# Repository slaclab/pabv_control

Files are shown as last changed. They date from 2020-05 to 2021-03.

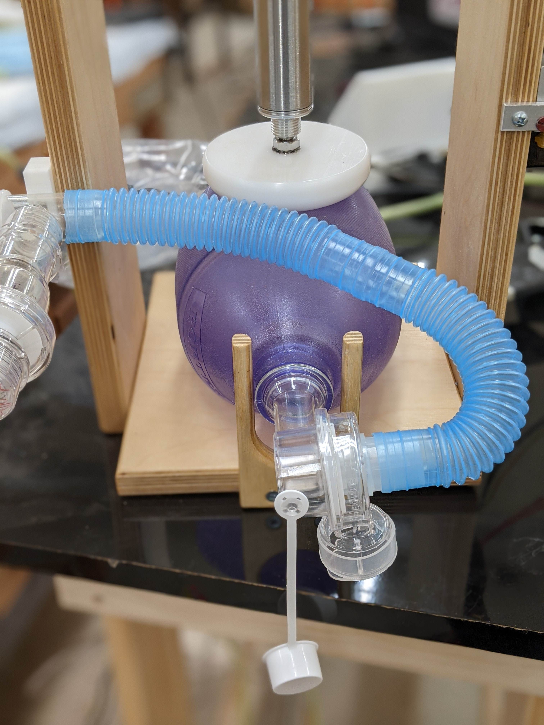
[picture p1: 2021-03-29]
ASV IP folder/Photos of assembled parts/PXL_20200915_001322814.PORTRAIT-01.COVER.jpg

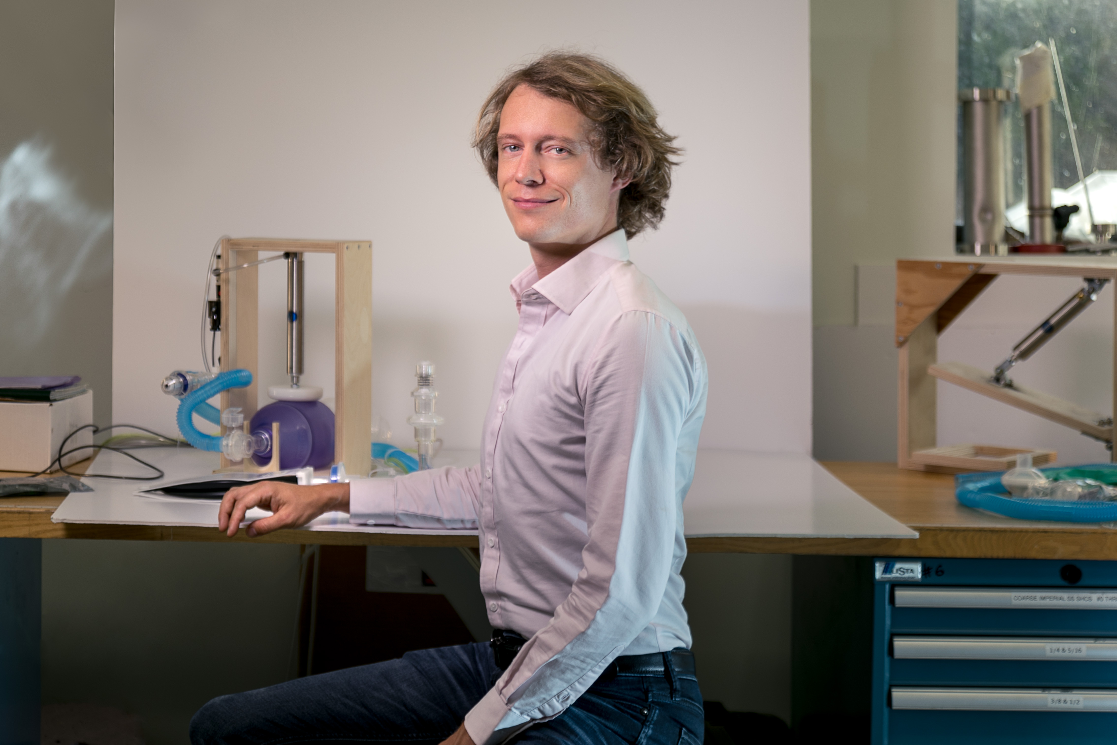
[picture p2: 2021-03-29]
ASV IP folder/Media materials/2020_0710_IR2_Ventilator_Gamazo_8752.jpg

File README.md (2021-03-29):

# Overview

This repository contains all hardware descriptions and software to build and control the SLAC
Acute Shortage Ventilator (ASV) developed to battle against the Covid crisis on a global scale.

All information on the project can be found at:

- [Media Announcement](https://www6.slac.stanford.edu/news/2020-08-13-slac-scientists-invent-low-cost-emergency-ventilator-and-share-design-free.aspx)
- [Official Paper](https://www.medrxiv.org/content/10.1101/2020.07.20.20158147v1)
- [Technology](http://techfinder.stanford.edu/technologies/S20-256_acute-shortage-ventilator)
- [DOECode](https://www.osti.gov/doecode/biblio/52411)
- [ASV Website](https://www.slac-asv.net/)

Documentation can also be found in the ASV IP folder directory of this repository

The content in this repository is licensed under a BSD 3-clause License. See LICENSE.txt for detail.

# Installation
### Getting the Code and dependencies
1. Install Anaconda3 (64-bit) for Windows 10 from here:
   https://www.anaconda.com/products/individual
and open a Anaconda Prompt
2. `conda install -y -c conda-forge git pyinstaller pyserial pyqt pyqtgraph`
3. `git clone https://github.com/slaclab/pabv_control`
4. `cd pabv_control`  
5. We now use submodules for various libraries, run this to pull them  
   `git submodule update --init --recursive`
##### Downloading arduin-cli
5. `bootstrap.py`
##### Compiling all sketches
6. `board_compile.py`

### Tested platforms
1.    Windows 10 64-bit
2.    Windows 10 32-bit
3.    Linux 64-bit
4.    MacOSX 64-bit

- Excutables built on Windows 10 32-bit may run on Windows 10 64-bit. Windows 7 or 8 support would require a native build.

### Packing the python client for distribution
- simply run the packaging scripts
- `pkg_gui.py`

### Wrapper scripts for arduino CLI

##### Show connected boards
- `board_list.py`
- this will create a standalone executable that can be copied to a USB stick

= example filename: `dist\client_py_Windows_64bit_v0.0.2-50-g3790d7b.exe`

Example output for an UNO

`Port Type              Board Name  FQBN            Core`

`COM3 Serial Port (USB) Arduino Uno arduino:avr:uno arduino:avr`

##### Upload compiled sketch
- `board_upload.py COM3 ambu_control_flow_cal`

Example output:

`Uploading sketch ambu_control_flow_cal to port COM3`

### Getting Running
- In Anaconda Prompt  
  - `cd pabv_control/python_client`  
  - `python client.py`

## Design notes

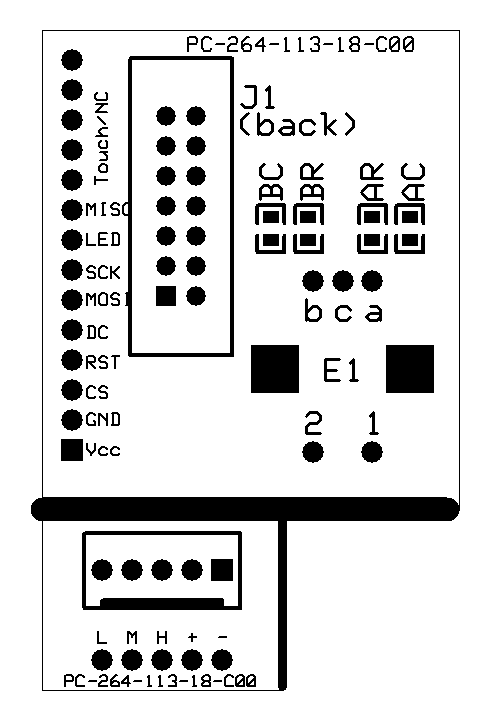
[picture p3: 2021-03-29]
ASV IP folder/Electronics/NanoShield_V03_breakouts.bmp

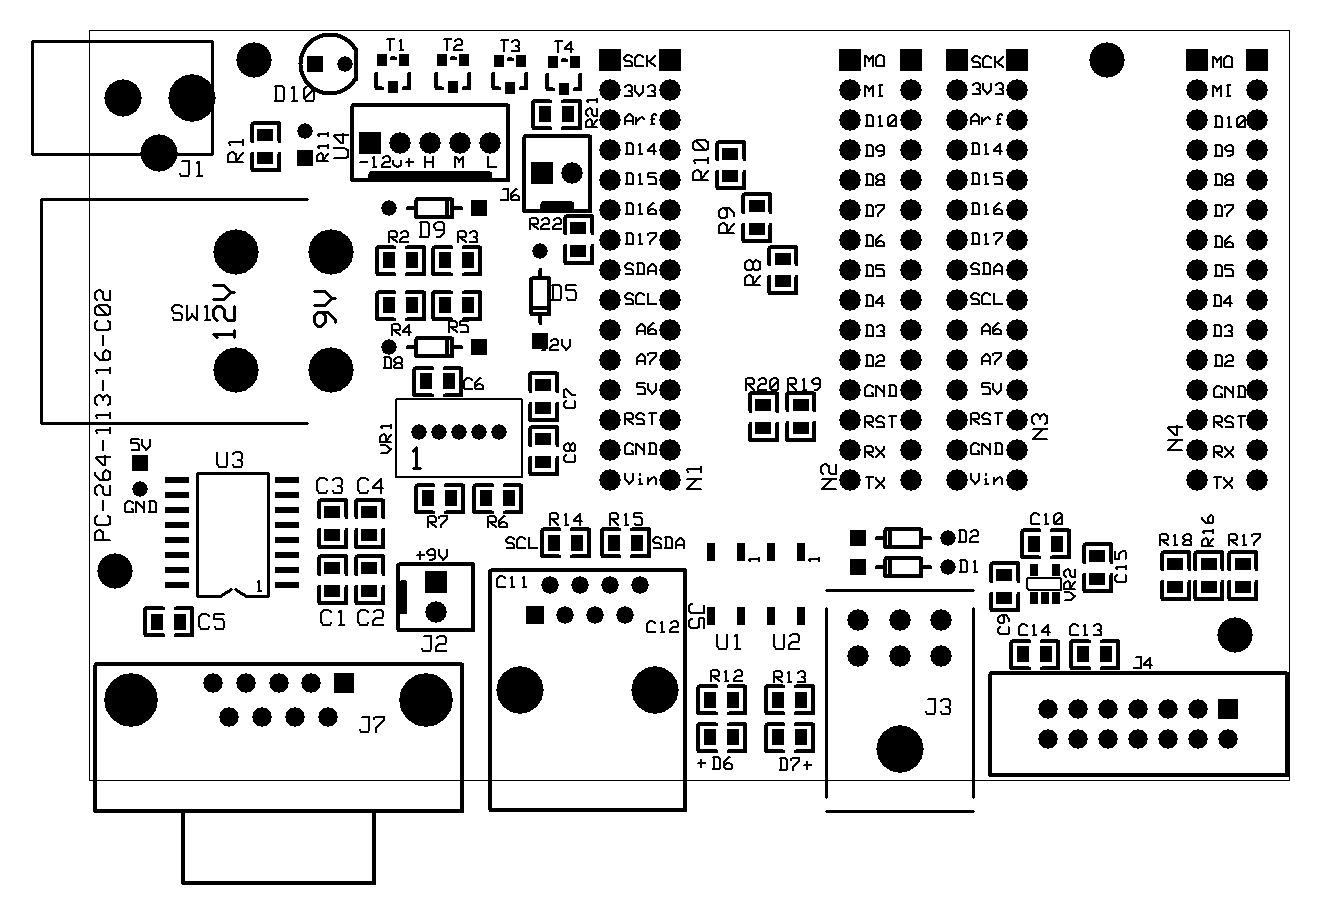
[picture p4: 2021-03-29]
ASV IP folder/Electronics/NanoShield_V03_pcb.bmp

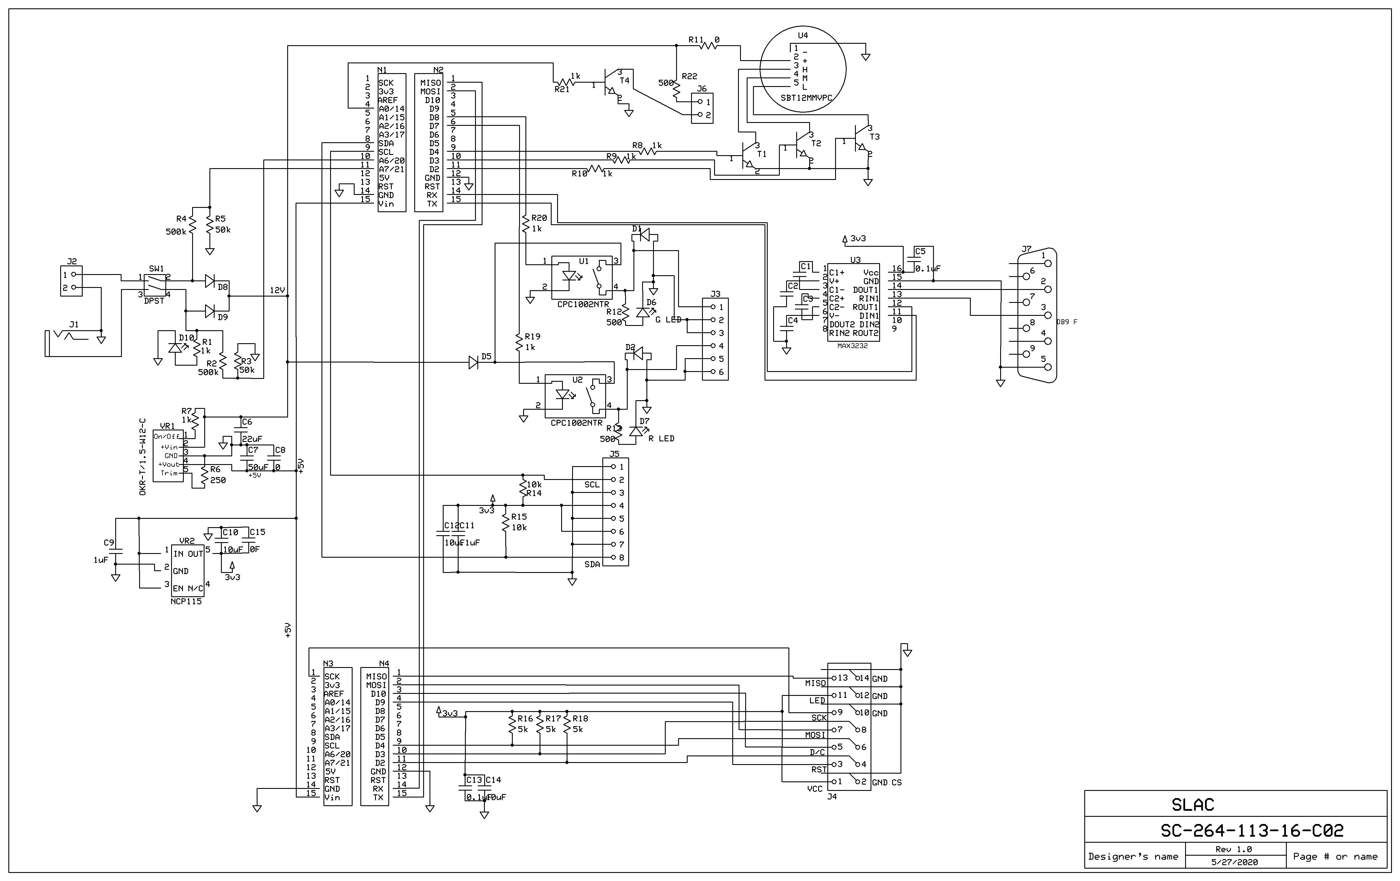
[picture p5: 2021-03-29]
ASV IP folder/Electronics/NanoShield_V03.bmp

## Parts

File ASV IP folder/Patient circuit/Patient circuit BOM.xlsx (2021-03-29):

Description | Link | Unit price | Qty | Total | Notes
PEEP valve | https://www.medline.com/sku/item/MDPPTX8501 | $22.26 | 2 | $44.53
HME filter | https://www.medline.com/sku/item/MDPDYNJAAHME1 | $2.12 | 1 | $2.12
MRI active patient circuit | https://www.medline.com/sku/item/MDPDYNJAA300NF | $23.64 | 1 | $23.64
Manual resuscitator w/ reservoir bag | https://www.medline.com/sku/item/MDPPTX8500P | $40.84 | 1 | $40.84
Straight connector with pressure port | https://www.medline.com/sku/item/MDPBXT004081 | $1.91 | 1 | $1.91
22-15-22 mm aerosol tee connector | https://www.medline.com/sku/item/MDPWST219 | $0.51 | 1 | $0.51
22mm cuff connector | https://www.medline.com/sku/item/MDPBXT001821 | $0.98 | 3 | $2.94
Exhalation filter | https://mms.mckesson.com/product/508994/Vyaire-Medical-303HEPA | $9.66 | 1 | $9.66
Spirometer | Alpha source inc p/n 8004382 (https://www.alphasource.com/) | $14.30 | 1 | $14.30
 |  |  | Total | $140.44

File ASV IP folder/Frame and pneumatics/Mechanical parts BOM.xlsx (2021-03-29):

Pneumatics | Seller | Part number | Cost
1/4" Polyflow Tube
3 way solenoid valve | Automation Direct | AVS-3312-24D | 35
Flow Control Valve OUT | Automation Direct | FVS14-18N | 6.5
Flow Control Valve IN | Automation Direct | FVR14-18N | 6.5
1/8in NPT Push2Connect | Automation Direct | MS14-18N
12V solenoid (to convert) | Automation Direct | AVC2-12D | 8.25
Binary Valve | Amazon | Beduan 2 Way Normally Closed DC 12V Electric Solenoid Air Valve 1/8" NPT | 11 | https://www.amazon.com/dp/B07N2DZ5FP/ref=pe_2640190_232586610_TE_dp_i1
1/8in NPT Exhaust Silencer | Automation Direct | SBF-18N

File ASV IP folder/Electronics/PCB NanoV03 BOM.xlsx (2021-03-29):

Nano Board |  |  | Sensor Board
Component | Value | Digikey Part Number | Ref Des | Part #
C1 | 0.1uF |  | U1 | DLC-L20D-D4
C2 | 0.1uF |  | U2 | SP110-SM02-R
C3 | 0.1uF |  | C1 | 0.1uF 0805
C4 | 0.1uF |  | C2 | 10uF 0805
C5 | 0.1uF |  | R1, R2 | 10K 0805
C6 | 22uF |  | R3 | 0 ohm 0805
C7 | 50uF |  | R4 | 100K 0805
C8 | 0 |  | J1 | RJLSE4118101-ND
C9 | 1uF
C10 | 10uF
C11 | .1uF
C12 | 10uF |  | LCD
C13 | 0.1uF | 805 | http://hiletgo.com/ProductDetail/2157216.html
C14 | 10uF | 805 | https://www.amazon.com/gp/product/B073R7BH1B/ref=ppx_yo_dt_b_asin_title_o00_s00?ie=UTF8&psc=1
C15 | 0F
D1 |  | 1N5817-TPCT-ND
D2 |  | 1N5817-TPCT-ND | Encoder
D5 |  | 1N5817-TPCT-ND | Digikey: PEC11R-4220K-S0024-ND
D6 | G LED | 732-4986-1-ND | https://www.digikey.com/products/en?keywords=PEC11R-4220K-S0024-ND
D7 | R LED | 732-4986-1-ND
D8 |  | 1N5817-TPCT-ND
D9 |  | 1N5817-TPCT-ND | Nano (x2)
D10 |  | 160-1852-ND | https://www.digikey.com/product-detail/en/arduino/ABX00027/1050-ABX00027-ND/10239968
J1 |  | 839-1512-ND
J2 |  | WM4800-ND
J3 |  | WM11867-ND | USB Serial Cable
J4 |  | ED10522-ND | https://www.amazon.com/dp/B006AA04K0/ref=pe_2640190_232586610_TE_dp_i1
J5 |  | A31407-ND
J6
J7 | DB9 F | 609-5189-ND | Ethernet Cable (for sensor box)
N1 |  | SAM1213-15-ND | Digikey: AE9961-ND
N2 |  | SAM1213-15-ND
N3 |  | SAM1213-15-ND
N4 |  | SAM1213-15-ND | Solenoid Cable to J3
R1 | 1k |  | WM13011-ND
R2 | 500k |  | We recommend upgrade to Digikey: WM15770-ND (requires different J3=WM1815-ND)
R3 | 50k
R4 | 500k
R5 | 50k
R6 | 250
R7 | 1k
R8 | 1k
R9 | 1k
R10 | 1k
R11 | 0
R12 | 500
R13 | 500
R14 | 10k
R15 | 10k
R16 | 5k
R17 | 5k
R18 | 5k
R19 | 1k
R20 | 1k
R21 | 1k
R22 | 500
SW1 | DPST | Z4419-ND
T1 |  | 1727-2956-1-ND
T2 |  | 1727-2956-1-ND
T3 |  | 1727-2956-1-ND
T4 |  | 1727-2956-1-ND
U1 | CPC1002NTR | CPC1002NTR
U2 | CPC1002NTR | CPC1002NTR
U3 | MAX3232 | 296-13095-1-ND
U4 | SBT12MMVPC | Mouser 539-SBT12MMVPC
VR1 | OKR-T/1.5-W12-C | 811-2782-ND
VR2 | NCP115 | NCP115ASN330T2GOSCT-ND

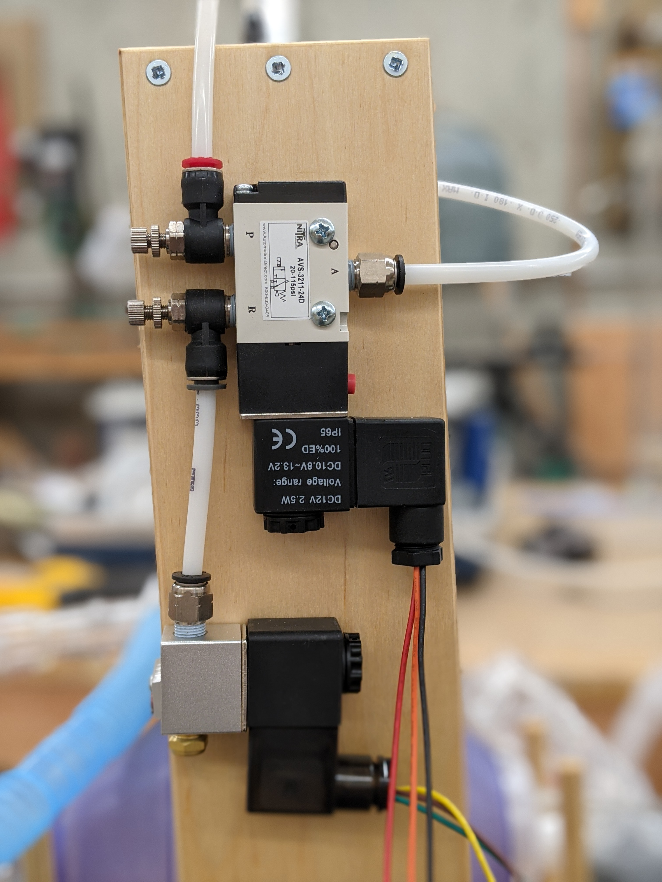
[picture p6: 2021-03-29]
ASV IP folder/Photos of assembled parts/PXL_20200915_001222688.PORTRAIT-01.COVER.jpg

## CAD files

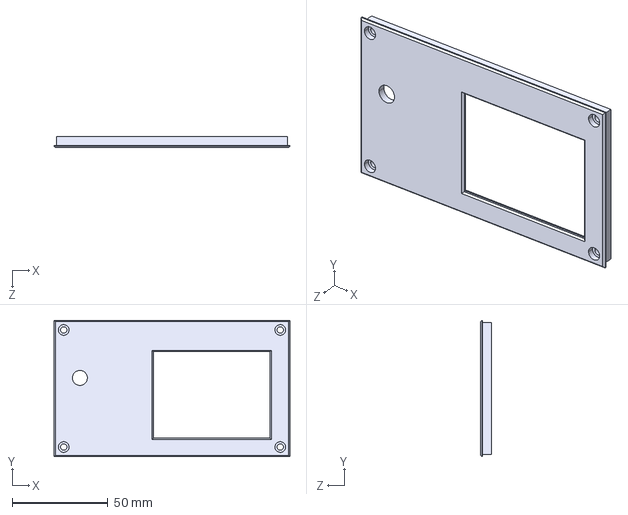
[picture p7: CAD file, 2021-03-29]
ASV IP folder/3-D printed parts/Nano Enclosure/ShieldEnclosure_Lid.STEP
123.4 x 71.4 x 5.97 mm

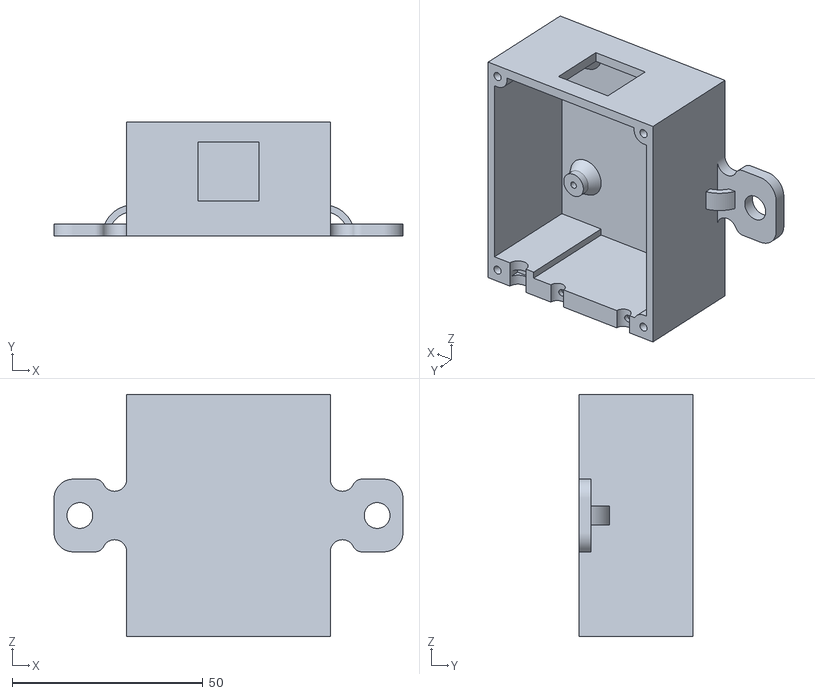
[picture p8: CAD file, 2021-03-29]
ASV IP folder/3-D printed parts/Sensor Enclosure/SensorBoard2_LowerBox.STL
91.4 x 29.8 x 63.5

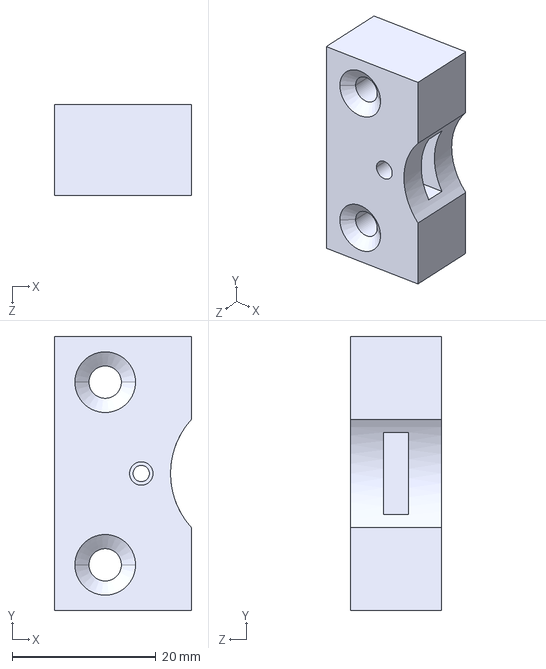
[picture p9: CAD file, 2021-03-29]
ASV IP folder/3-D printed parts/THolder.STEP
19.1 x 38.1 x 12.7 mm

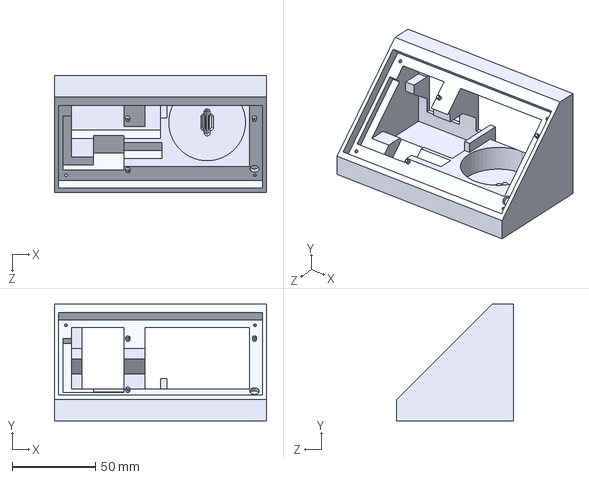
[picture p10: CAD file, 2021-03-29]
ASV IP folder/3-D printed parts/Nano Enclosure/ShieldEnclosure_Upper.STEP
127.0 x 69.8 x 69.9 mm

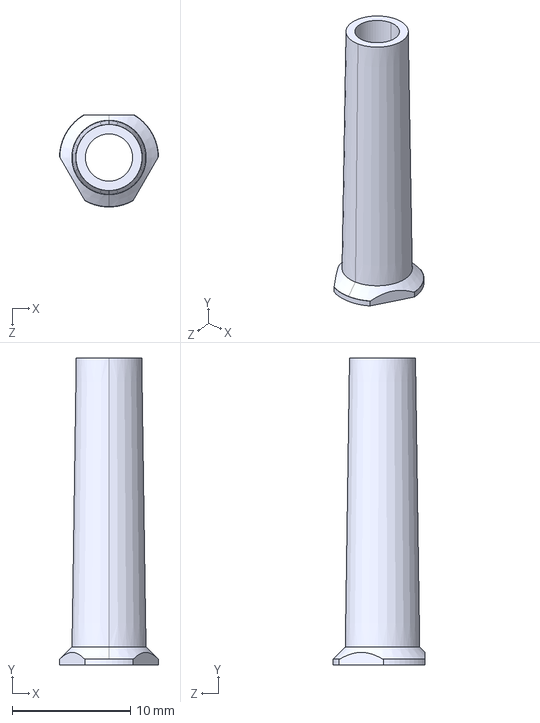
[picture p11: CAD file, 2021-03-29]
ASV IP folder/3-D printed parts/PEEP to PIP converter 26mm.STEP
8.39 x 26.0 x 7.79 mm

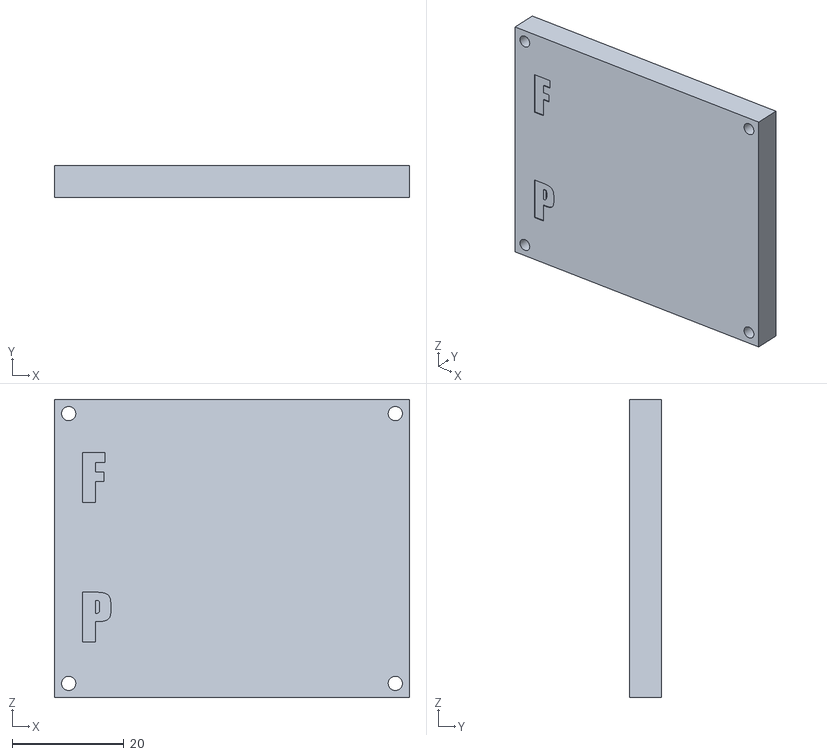
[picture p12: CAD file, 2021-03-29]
ASV IP folder/3-D printed parts/Sensor Enclosure/SensorBoard2_Lid.STL
63.5 x 5.72 x 53.3

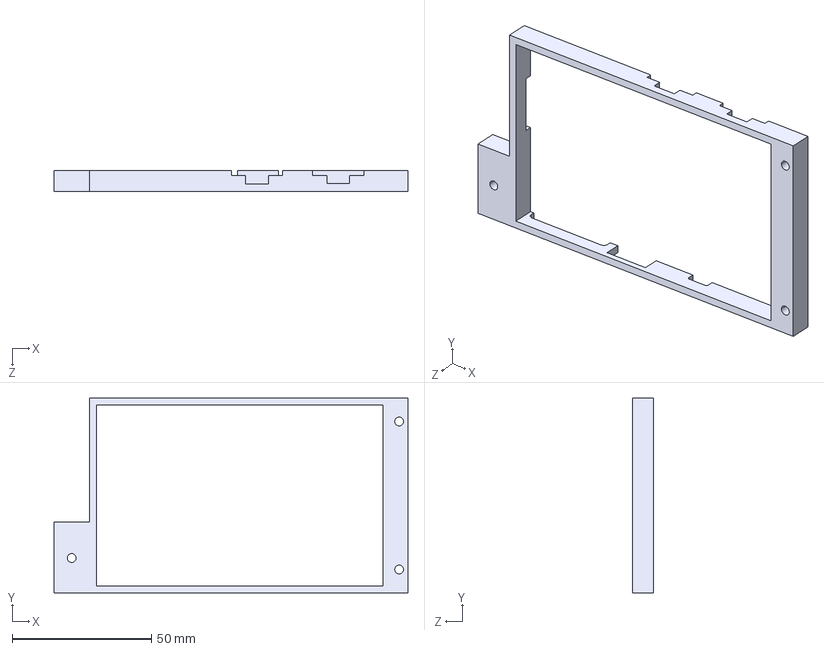
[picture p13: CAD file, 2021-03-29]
ASV IP folder/3-D printed parts/Nano Enclosure/ShieldEnclosure_Mid.STEP
127.0 x 69.9 x 7.62 mm

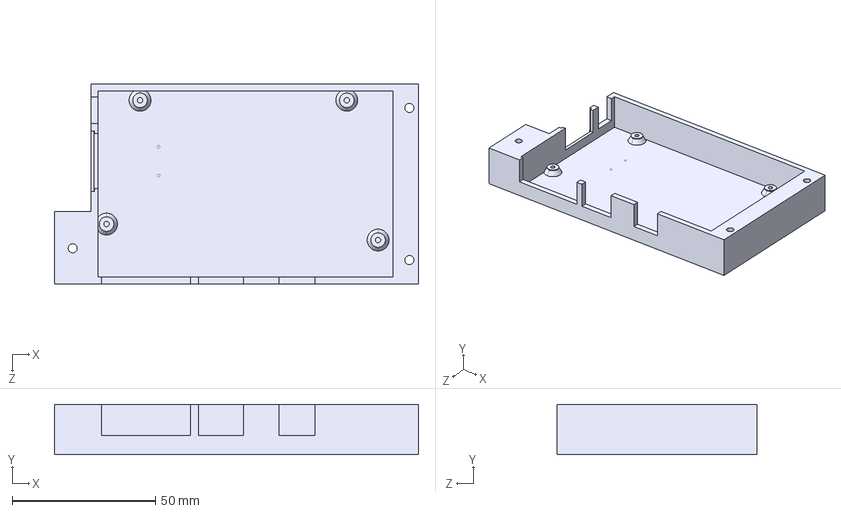
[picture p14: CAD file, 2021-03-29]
ASV IP folder/3-D printed parts/Nano Enclosure/ShieldEnclosure_Lower.STEP
127.0 x 17.5 x 69.9 mm

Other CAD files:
ASV IP folder/3-D printed parts/Nano Enclosure/ShieldEnclosure_Lid.STL
ASV IP folder/3-D printed parts/Nano Enclosure/ShieldEnclosure_Lower.STL
ASV IP folder/3-D printed parts/Nano Enclosure/ShieldEnclosure_Mid.STL
ASV IP folder/3-D printed parts/Nano Enclosure/ShieldEnclosure_Upper.STL
ASV IP folder/3-D printed parts/PEEP to PIP converter 26mm.STL
ASV IP folder/3-D printed parts/THolder.STL

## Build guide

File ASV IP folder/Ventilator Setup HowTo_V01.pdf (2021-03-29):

# Visual Setup Guide

## PABV Ventilator Version 1.0

# Table Of Contents

## 1. Unpacking and taking inventory 2. Setup Pneumatics

## 1. From regulated “hospital air” or compressor 2. From high pressure cylinder bottle

## 3. Setup Patient Circuit 4. Setup Electronics

# 1) Unpacking and Taking Inventory

# 2.1) Connect pneumatic air supply to hospital air

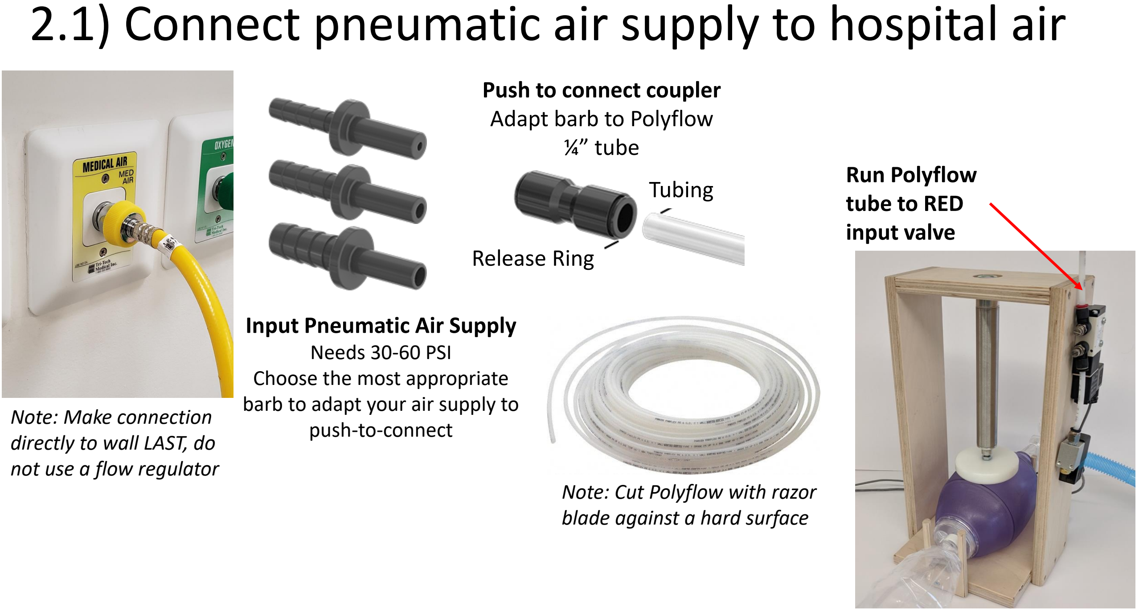
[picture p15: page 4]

Input Pneumatic Air Supply Needs 30-60 PSI
Choose the most appropriate barb to adapt your air supply to push-to-connect

Run Polyflow
tube to RED
input valve

Push to connect coupler
Adapt barb to Polyflow
¼” tube

Note: Cut Polyflow with razor blade against a hard surface

Tubing

Release Ring

Note: Make connection
directly to wall LAST, do
not use a flow regulator

# 2.2) Connect pneumatic air supply to other

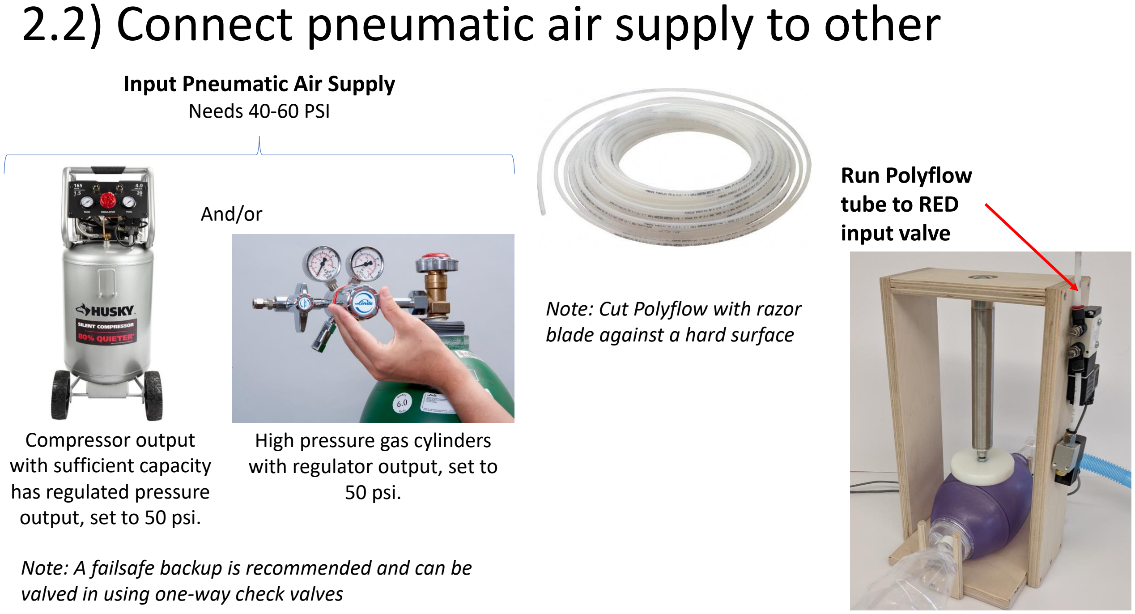
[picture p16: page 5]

Input Pneumatic Air Supply Needs 40-60 PSI

Run Polyflow
tube to RED
input valve

Note: Cut Polyflow with razor blade against a hard surface

High pressure gas cylinders with regulator output, set to 50 psi.

Compressor output
with sufficient capacity
has regulated pressure
output, set to 50 psi.

Note: A failsafe backup is recommended and can be valved in using one-way check valves

And/or

# 3) Patient Circuit

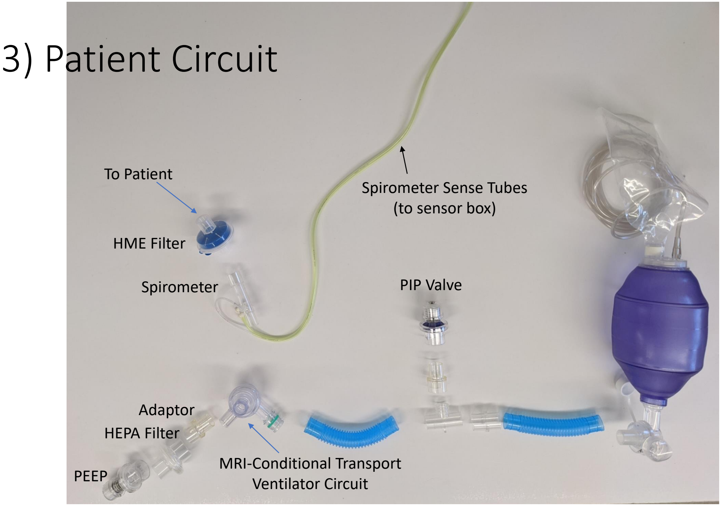
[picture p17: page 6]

Spirometer Sense Tubes
(to sensor box)

HME Filter

To Patient

Spirometer

PEEP

HEPA Filter

Adaptor

MRI-Conditional Transport
Ventilator Circuit

PIP Valve

# 4) Setup Electronics

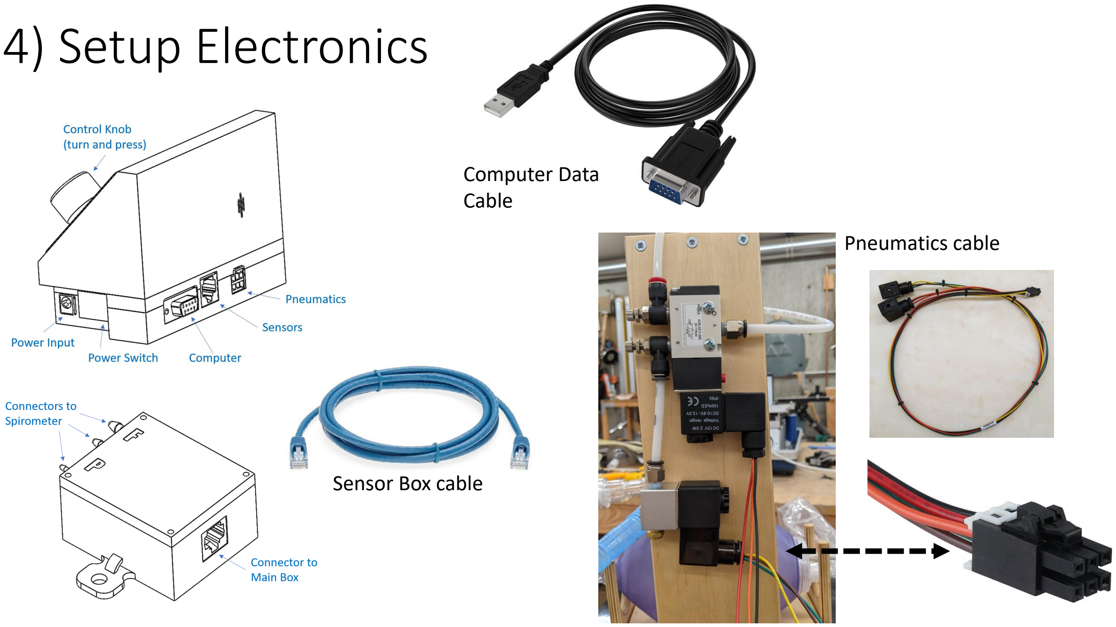
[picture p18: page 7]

Computer Data
Cable

Sensor Box cable

Pneumatics cable

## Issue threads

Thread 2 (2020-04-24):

slaclab/pabv_control #2: COM ports

bungernut, 2020-04-24:
We should look into something that tries a bunch or com ports or takes an argv, but leaves this as default.

https://github.com/slaclab/pabv_control/blob/a0b400357dda1c3e6de72b4bdc33c25a4d606cd0/python_client/client_dual.py#L27

bungernut, 2020-04-26:
Working on this in branch https://github.com/slaclab/pabv_control/tree/bung/gui_com_selector

mwittgen, 2020-04-29:
Should work if the vendor/product ID of the Arduinos used  are known by the GUI for COM lookup
`
import serial.tools.list_ports
for port in serial.tools.list_ports.comports():
    print(port.vid,port.pid,port.serial_number,port.manufacturer,port)
`
For an original UNO this returns:
9025 67 75433303631351D0E140 Arduino (www.arduino.cc) /dev/ttyACM0 - ttyACM0
Also no need to hard wire the /dev/tty on Linux
What about multiple Arduinos connected?

mwittgen, 2020-04-29:
Here's a list of a lot of known board VID/PID:
https://github.com/arduino/ArduinoCore-avr/blob/master/boards.txt

bungernut, 2020-04-29:
@mwittgen if you're comfortable working w/ pyqt (I'm not very) it might be nice to integrate this feature. Merging this branch is probably out of the question for other reasons, but this feature does work as I have it here I think.

mwittgen, 2020-04-30:
OK. Assign it to me.

slacrherbst, 2020-04-30:
The vendor ID approach is interesting. I use that at home to deal with multiple devices connected on usb to serial devices. It does assume the device type is know ahead of time which may not always be the case once we move to a usb to serial converter which have pretty generic device type IDs

slacrherbst, 2020-04-30:
It may also only work with linux based sytems

mwittgen, 2020-04-30:
@slacrherbst How does the final system look like? You will use the RX/TX pins for serial into a PC and no USB?

slacrherbst, 2020-04-30:
We will use standard RS232 and the user will supply a usb to serial adapter.

mwittgen, 2020-04-30:
OK. Going to add a MAX3232 to my test Uno and a USB-to-RSR32. What's reason not to use the USB directly? Packaging?

bungernut, 2020-04-30:
@mwittgen We wanted to be able to connect a laptop with the program running, and it would just receive serial input. So with an external USB-Serial adapter staying with the computer, the COM port stays the same and open. You can remove the connection from one device and plug straight into another and be up and running. 

If you think there is a better way, happy to hear it.

mwittgen, 2020-05-15:
Brian already implemented this. Next step: test and merge the branch add_serial.

mwittgen, 2020-06-02:
Closing. We are auto detecting the port.

closed 2020-06-02 by mwittgen

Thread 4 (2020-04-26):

slaclab/pabv_control #4: Log reliability

bungernut, 2020-04-26:
Marty says the log is not bullet proof, not sure what that means.

marty-pmr, 2020-04-26:
Opening a file should be confirmed, as should closing. Opening twice seems to make a mess. The file itself seems pretty good, but should be well defined as to what it is.

mwittgen, 2020-05-15:
@marty-pmr @bungernut where do we stand on this?

bungernut, 2020-05-15:
I think only Ryan knows, maybe Marty does... probably not addressed though

marty-pmr, 2020-05-16:
I think this is still open. Not sure whether we need logging - perhaps for debugging???

mwittgen, 2020-05-16:
It should be removed then, the current version crashes. A true login feature might be better implemented on the arduino (not suggesting this). The client GUI as of now is stateless and adding file logging adds a dependency on the Win 10 laptop state. As of now the client could simply run from a USB stick and does not depend on any external  storage state and resources.

marty-pmr, 2020-05-16:
I have been using the log files to calibrate the spirometer. There could be ways of doing it without the log files…m

mwittgen, 2020-06-05:
Closing this for now. Has been fixed in devel.

closed 2020-06-05 by mwittgen

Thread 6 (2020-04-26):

slaclab/pabv_control #6: memory?

bungernut, 2020-04-26:
I see lists are use to append data to. 
https://github.com/slaclab/pabv_control/blob/052e1d21fd8dd91c379374a21a47d0522e79b7ec/python_client/ambu_control.py#L99
Might make sense to use finite (numpy) arrays and let old data fall off.
Of course saving to file would still keep historical data.

bungernut, 2020-05-15:
I'm trying to implement a numpy FIFO class in ambu_contorl.py since that's where the data is. However this is not exactly straightforward in the abstraction to the GUI... I suspect @mwittgen knows both numpy and how the gui works enough to help?

bungernut, 2020-05-15:
well lets just say the class looks somethign like this
```
class npfifo:
    def __init__(self, num_parm, num_points):
        self._n = num_parm
        self._x = num_points
        self.A = numpy.zeros((self._n, self._x))
        self._i = 0
    
    def append(self, X):
        if len(X) != self._n:
            print("Wrong number of parameters to append, ignoring")
        # Move the data in the buffer
        self.A[:,:-1] = self.A[:,1:]
        # add the data to the end of the buffer
        self.A[:,-1] = X
        # increment number of 
        self._i += 1 
    
    def clear(self):
        self.A = 0.0
        self._i = 0
```

bungernut, 2020-05-15:
Adding something to get the data and we could check if there is enough data?
```
class npfifo:
    def __init__(self, num_parm, num_points):
        self._n = num_parm
        self._x = num_points
        self.A = numpy.zeros((self._n, self._x))
        self._i = 0
    
    def append(self, X):
        if len(X) != self._n:
            print("Wrong number of parameters to append, ignoring")
        # Move the data in the buffer
        self.A[:,:-1] = self.A[:,1:]
        # add the data to the end of the buffer
        self.A[:,-1] = X
        # increment number of 
        self._i += 1 
    
    def clear(self):
        self.A = 0.0
        self._i = 0
        
    def get_data(self):
        if self._i > 1:
            return self.A[:,-min(self._i, self._x):]
        else:
            return None
```

bungernut, 2020-05-15:
@mwittgen @slacrherbst We need to talk about this, in particular Matthias, if we're to keep flexible data stream this class seems incompatible with that goal.  Numpy in some sense becomes even less so than the current dict of lists... When is good time tomorrow morning?

bungernut, 2020-05-15:
@slacrherbst have a look at this 313778c89ca765070fd627bb1ee824a0e2e16c9e

mwittgen, 2020-05-17:
@bungernut can this be closed?

bungernut, 2020-05-17:
@mwittgen probably, assuming you're happy with the array structure.

closed 2020-05-17 by mwittgen

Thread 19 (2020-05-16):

### ISSUE TITLE
Move important data 1

### ISSUE THREAD

**Issue by marty-pmr** [slaclab/pabv_control#19]
In the Arduino, for each cycle, pick off measured PIP and PEEP and send to python.

**Comment by mwittgen** [comment]
@marty-pmr with more data sent the serial line might not keep up:
57600 bits / sec = 5760 bytes /sec (start,stop,8 data bits) 
limiting the message size to 57 bytes at 100Hz.
Is the 100Hz data rate a strict requirement? Or should certain channels be sent at different rates?

**Comment by marty-pmr** [comment]
The cycle status data should move once every 2-3 seconds. Should not be a problem.

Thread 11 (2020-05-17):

### ISSUE TITLE
Pressure, Flow and Volume Calcs

### ISSUE THREAD

**Issue by marty-pmr** [slaclab/pabv_control#11]
I think it would be a good move to send the calcs for Pressure, Flow, and Volume (PFV) to the Arduino. We will need it for Brian's display, and I really want to do an experiment related to the FDA papers: Set a Vmax parameter in the GUI and close the valve when V>Vmax. 
Then 3 numbers flow from the Arduino towards the GUI.  Is there any possibility of straing the Arduino doing this?

**Comment by mwittgen** [comment]
@slacrherbst I guess this can be closed as well?

**Comment by mwittgen** [comment]
Looks like this is done. Reopen otherwise.

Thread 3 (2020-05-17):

### ISSUE TITLE
scrolling display

### ISSUE THREAD

**Issue by bungernut** [slaclab/pabv_control#3]
>10Hz (25Hz preferable) for the waveforms.

**Comment by marty-pmr** [comment]
I hope the Python has a enough power for this - I don't see why not. The lack of a real scrolling display seems a little archaic.

**Comment by marty-pmr** [comment]
I think my laptop problem has little to do with GUI.

**Comment by mwittgen** [comment]
@bungernut The display is scrolling in the latest version. Can you confirm and close?

**Comment by bungernut** [comment]
master or devel or both?

**Comment by mwittgen** [comment]
They are in sync as of now.

**Comment by bungernut** [comment]
confirmed w/ MIB using Uno this morning

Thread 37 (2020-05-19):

### ISSUE TITLE
Ventilation hangs when python client starts

### ISSUE THREAD

**Issue by kernal42** [slaclab/pabv_control#37]
When a user starts up the python GUI, the arduino-controlled ventilation hangs for O(5) seconds.

**Comment by mwittgen** [comment]
Is this through a USB connection to the arduino? USB resets the board and there is a 5 seconds startup delay on the arduino.

**Comment by kernal42** [comment]
Yes, this is with USB connection.  That sounds like the explanation!

**Comment by mwittgen** [comment]
Closing this issue. The arduino uptime should be displayed in the GUI though.

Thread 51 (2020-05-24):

slaclab/pabv_control #51: Communication???

marty-pmr, 2020-05-24:
Found the time histories stuck. Python had no obvious problems. Could sort of stop/start cycling....Turn it off and a minute later it was going again.

mwittgen, 2020-05-24:
Seems a duplicate in some sense of closes issues#29 and #30. Instead of suppressing "debug" messages the should have a counter if packets are scrambled. It could be related to this issue.

marty-pmr, 2020-05-25:
Happened again this morning. Is there anything significant about a time of 88347.3 seconds Nano uptime?Is some 16 bit integer overflowing?

mwittgen, 2020-05-25:
It's a 32 bit millisecond counter and wraps around every 49 days.We really should keep statistics in the GUI on scrambled packets and try to guess  "package loss" by comparing excepted number of data packets, roughly GUI uptime compared to packets seen from the arduino.

mwittgen, 2020-06-05:
Communication was largely reworked.

closed 2020-06-05 by mwittgen

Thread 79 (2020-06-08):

### ISSUE TITLE
GUI fix values changing under user

### ISSUE THREAD

**Issue by bungernut** [slaclab/pabv_control#79]
I would propose the following to fix the user's input being updated every status update (1Hz), making it impossible to change values. 

Add state variables to control_gui.py
```
--- a/python_client/control_gui.py
+++ b/python_client/control_gui.py
@@ -112,10 +112,15 @@ class ControlGui(QWidget):
         self.ambu = ambu
         self.ambu.setDataCallBack(self.dataUpdated)
         self.ambu.setStateCallBack(self.stateUpdated)
+        self.respRateVal  = 0.0
         self.respRate     = None
+        self.inhTimeVal   = 0.0
         self.inhTime      = None
+        self.volInhTholdVal = 0.0
         self.volInhThold  = None
+        self.pipMaxVal    = 0.0
         self.pipMax       = None
+        self.volMaxVal    = 0.0
```

Check if value changes from ambu before updating
```
@@ -775,11 +781,16 @@ class ControlGui(QWidget):
     def stateUpdated(self):
...
+        if self.ambu.volMax != self.volMaxVal:
+            self.updateVolMax.emit("{:0.1f}".format(self.ambu.volMax))
+            self.volMaxVal = self.ambu.volMax
```

Need to figure out a way to check if text() disagrees w/ stored value and make the box red or something, and then I would say a 10 second timeout should be applied to reset the text if it's not being changed anymore and it disagrees.

**Comment by slacrherbst** [comment]
The ambu_control.py file already does this. The problem is i got lazy and over used the callback. Issue_70 branch will address this.

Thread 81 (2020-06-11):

### ISSUE TITLE
Speeding up matplotlib plots

### ISSUE THREAD

**Issue by bungernut** [slaclab/pabv_control#81]
I'm getting 0.143s execute times for the `dataUpdated()` method which draws the plots. I'm hoping to shave a lot of cycles by finding a more efficient method

**Comment by bungernut** [comment]
Currently investigating this
https://bastibe.de/2013-05-30-speeding-up-matplotlib.html

**Comment by mwittgen** [comment]
pyqtgraph branch is available speeding up plotting.

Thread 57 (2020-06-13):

### ISSUE TITLE
Flattop Valve

### ISSUE THREAD

**Issue by marty-pmr** [slaclab/pabv_control#57]
We want to add the option of a second valve controlling the exhaust timing to make volume control really work.
To keep things straight, the existing valve is called Main, and its control does not change at all.
The new valve, called Exhaust, is a separate pin on the Arduino. 
Exhaust turns ON at the end of tinspiration (usually 1 second)
Exhaust turns OFF at the beginning of a cycle. (Either by the timer or a voluntary breath)

**Comment by slacrherbst** [comment]
Addressed in #80

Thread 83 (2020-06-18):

### ISSUE TITLE
Volume Correction

### ISSUE THREAD

**Issue by marty-pmr** [slaclab/pabv_control#83]
The existing calculation in the Python should be something like Varduino = Vmax+Voffset.
Let's try Varduino =Vmax - (-0.0011*Vmax^2 + 0.3005*Vmax + 87.95) +Voffset

**Comment by bungernut** [comment]
The arduino does not take input one parameter, it takes in Vmax and Voffset. TO do this, I would need to change the ardunio code.

Since the GUI reflects the values in the arduino, not something abstracted, there is no easy way to implement this in my opinion.

**Comment by marty-pmr** [comment]
Aha, you are right. Curses, foiled again.

**Comment by slacrherbst** [comment]
This is done right?

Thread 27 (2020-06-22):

### ISSUE TITLE
NANO EEPROM is more complicated

### ISSUE THREAD

**Issue by bungernut** [slaclab/pabv_control#27]
Need to use a EEPROM emulator and flash memeory

https://github.com/cmaglie/FlashStorage

Limits writes to 10000 and these values will be reset every flash, but persist through resets.

**Comment by bungernut** [comment]
Starting to address this 737ba07ef7644da8180830051714293dee7cef32

**Comment by sluitz** [comment]
Add a serial EEPROM (e.g. Microchip 24LC256) to the shield?  >1E6 erase/write cycles. Still needs library but at least it's not messing with the flash and persistent through firmware upgrades.

**Comment by bungernut** [comment]
I see no harm in laying it out in the next board, if we use it TBD

**Comment by mwittgen** [comment]
We are using the internal nano flash memory.

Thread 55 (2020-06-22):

### ISSUE TITLE
Measure IT time in volume mode

### ISSUE THREAD

**Issue by bungernut** [slaclab/pabv_control#55]
If we go ahead with GUI modes for pressure control and volume control.

Volume control compresses the bag until a volume threshold is reached. This time depends on the patient lung compliance and the leak valve setting. It is necessary in our design to tune the input leak valve to achieve near the specified inhalation time (IT). For that reason it would be nice to know when the relay state closes and opens to display the time in the GUI.

**Comment by slacrherbst** [comment]
Pull request #80 adds a currState property to the AmbuControl class which provides access to the current state of the arduino cycle control state machine. 0 = paddle down, 1 = paddle up, 2 = paddle hold.

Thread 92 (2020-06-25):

### ISSUE TITLE
Changes For Alarm Display

### ISSUE THREAD

**Issue by marty-pmr** [slaclab/pabv_control#92]
1. Remove CLEAR from green banner.
2. for PIP MAX (Red) "Peak Patient Inspiratory pressure exceeded. Check PIP Valve"
3. Vol Low Alarm (Red) "Low Tidal Volume. Check Ventilator, patient circuit"
4. 12 V (Red) "Electrical power lost"
5. 9 V (Yellow) "Alarm battery low. Replace soon"
6. Pressure Low (Red) "Patient Inspiratory Pressure Low, Check patient circuit"
7. Peep Min (Yellow) "Pressure below PEEP. Check patient circuit"

**Comment by mwittgen** [comment]
@marty-pmr currently only one alarm condition is displayed on the banner. How do the alarm and warning condition rank?
alarms have a higher display priority than warnings, but we would need to sort alarm and warning conditions.

**Comment by marty-pmr** [comment]
Hi Matthias,

I would like to try scrolling through alarms and warnings, say 2 second shots…

Thanks,

Marty

**Comment by mwittgen** [comment]
Addressed in latest devel

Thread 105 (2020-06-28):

slaclab/pabv_control #105: Make "adaptive" algorithm compatible with pressure-limited ventilation mode

kernal42, 2020-06-28:
When in pressure ventilation mode, the user sets the desired volume to something higher than the system is likely to reach (such as 700 mL), and the piston stroke ends when the max PIP pressure is reached.  With these settings, the volume correction factor drifts off with every stroke and becomes unreasonably large, providing poor system response if the user switches to a volume ventilation mode later.  

The correct behavior is probably to apply the adaptive algorithm and modify the volume offset only if the piston stroke was stopped by reaching the maximum volume.  In all other cases (inhalation time reached before max volume, or PIP reached before max volume) the adaptive algorithm should not be trying to learn.

bungernut, 2020-06-29:
I'm still confused by this. If we're in pressure mode, the "learning" should not matter. What it is supposed to do in pressure mode is squeeze until the time set by IT is reached. This is what the learning would do anyway.

kernal42, 2020-06-29:
There are two scenarios where I think this modification is relevant:
1) If the user switches from a pressure mode to a volume mode.  Long-running in the pressure mode will cause the correction factor to become very large.  When switching to a volume mode, now the calculation employs this unreasonably large correction factor and gives poor results until correction factor returns to baseline (presumably time proportional to amount of time running in pressure mode).  
2) The user has selected tight bounds on both volume and pressure.  If the system ever triggers on pressure, then the correction factor will receive a shock (as above) and the real volume trigger value will deviate.  

Note: (1) would also be solved by resetting the correction factor whenever use settings change.  I'm not sure that's a great solution though.

bungernut, 2020-06-29:
For one we know if the end result of the stroke comes from the Vmax. In that case only should we be applying the learning algorithm.  I think this fixes both cases?

There should perhaps be some range of values so that calculations do not run away causing some malloc or other C++ error.

bungernut, 2020-06-29:
Ok, i see that's exactly what you proposed. Are you sure that's not the way it's implemented?

bungernut, 2020-06-30:
Ryan, can you look into this?

marty-pmr, 2020-07-02:
I will try to define the two modes. m

slacrherbst, 2020-07-07:
Addressed in #107

closed 2020-07-07 by slacrherbst

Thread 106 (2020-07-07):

### ISSUE TITLE
Separate Volume and Pressure Modes

### ISSUE THREAD

**Issue by marty-pmr** [slaclab/pabv_control#106]
For mostly keeping the operation of the ASV similar to that of commercial ventilators, lets implement separate Volume and Pressure modes.

There should be a mode switch, logically the same as On/Off in the GUI and reflected in the Arduino.

In Volume mode:  As things are now

In Pressure mode:  Ignore the VolMaxAdj (ie do not stop the piston if VolMaxAdj is reached) parameter and do not change it.

**Comment by kernal42** [comment]
Note: If Issue #105 is resolved as suggested, it should be unnecessary for the mode change to explicitly freeze VolMaxAdj.

**Comment by slacrherbst** [comment]
Set volmax to 800 for this mode.

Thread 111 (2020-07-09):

### ISSUE TITLE
GUI Parameter Names

### ISSUE THREAD

**Issue by bungernut** [slaclab/pabv_control#111]
PMax not PIPMax

**Comment by marty-pmr** [comment]
Also:
On pressure plot legend: P_thresh_hi ->PMax
P_thresh_low -> Vol Inh P


On inputs: V_Max ->VMax
On Volume plot legend: V_threshold_high ->VMax

On Expert Tab: Hide PiP Offset (not in use)

Format I:E

**Comment by bungernut** [comment]
@marty-pmr `P_thresh_low -> Vol Inh P`
Vol looks a lot like volume, is there any other ideas?

**Comment by bungernut** [comment]
new branch issue111 for this

**Comment by bungernut** [comment]
@marty-pmr how about `PSV Trg`?

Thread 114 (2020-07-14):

slaclab/pabv_control #114: Change Volume Alarms

marty-pmr, 2020-07-14:
Based on EURS requirements, lets modify teh volume alarms:
In Volume mode, generate Low Volume (Medium Priority) at or below 80% VMax
Generate High Volume alarm at 120% of VMax.
As always, this in the On state after 5 breaths....
In Pressure, stay as is with the same Low Volume alarm.

slacrherbst, 2020-07-17:
Just to clarify. We need to add a volumeHigh alarm which did not exist before. Is this an alarm or warning.

Volume low goes from an alarm to a warning? In both modes?

marty-pmr, 2020-07-17:
Yes. In Volume mode, low and high are medium priority.
In pressure mode, volume below 250 ml is high priority.

bungernut, 2020-07-17:
This needs expanded to do this presumably:
https://github.com/slaclab/pabv_control/blob/d83d117002328973569dc3e3ef2438cf2efa231c/arduino/libraries/ambu_common/CycleControl.cpp#L180

PR #115 (2020-07-18): Update alarms
Closes #114
closed 2020-07-18 by slacrherbst

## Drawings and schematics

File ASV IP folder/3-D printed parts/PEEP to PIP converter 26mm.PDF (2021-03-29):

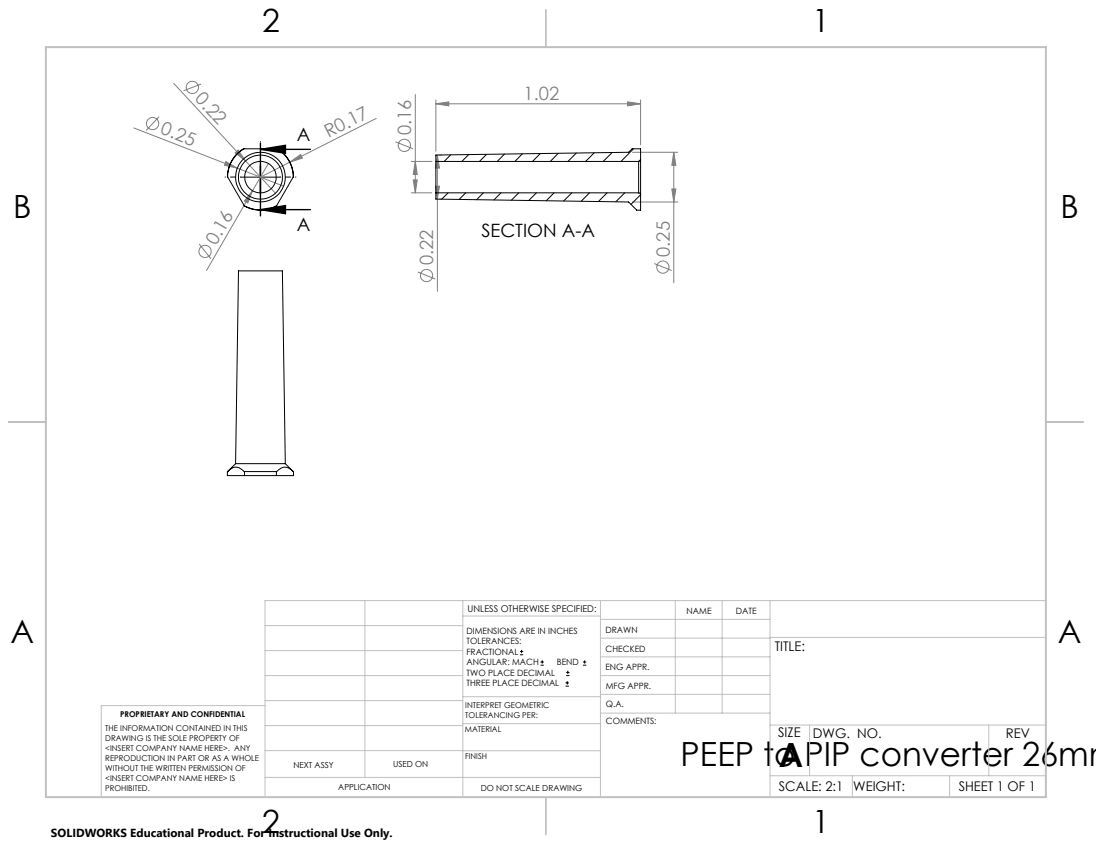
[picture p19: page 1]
SECTION A-A

UNLESS OTHERWISE SPECIFIED: | | NAME | DATE
DIMENSIONS ARE IN INCHES TOLERANCES: FRACTIONAL ANGULAR: MACH BEND TWO PLACE DECIMAL THREE PLACE DECIMAL | DRAWN

CHECKED | | | TITLE:

ENG APPR.
MFG APPR.

INTERPRET GEOMETRIC TOLERANCING PER: | Q.A.
MATERIAL | | SIZE A | DWG. NO. | REV

PROPRIETARY AND CONFIDENTIAL
THE INFORMATION CONTAINED IN THIS
DRAWING IS THE SOLE PROPERTY OF
<INSERT COMPANY NAME HERE>. ANY
REPRODUCTION IN PART OR AS A WHOLE
WITHOUT THE WRITTEN PERMISSION OF
<INSERT COMPANY NAME HERE> IS
PROHIBITED.

COMMENTS:
PEEP to PIP converter 26mm

NEXT ASSY | USED ON | FINISH

APPLICATION | DO NOT SCALE DRAWING | | SCALE: 2:1 | WEIGHT: | SHEET 1 OF 1

SOLIDWORKS Educational Product. For Instructional Use Only.

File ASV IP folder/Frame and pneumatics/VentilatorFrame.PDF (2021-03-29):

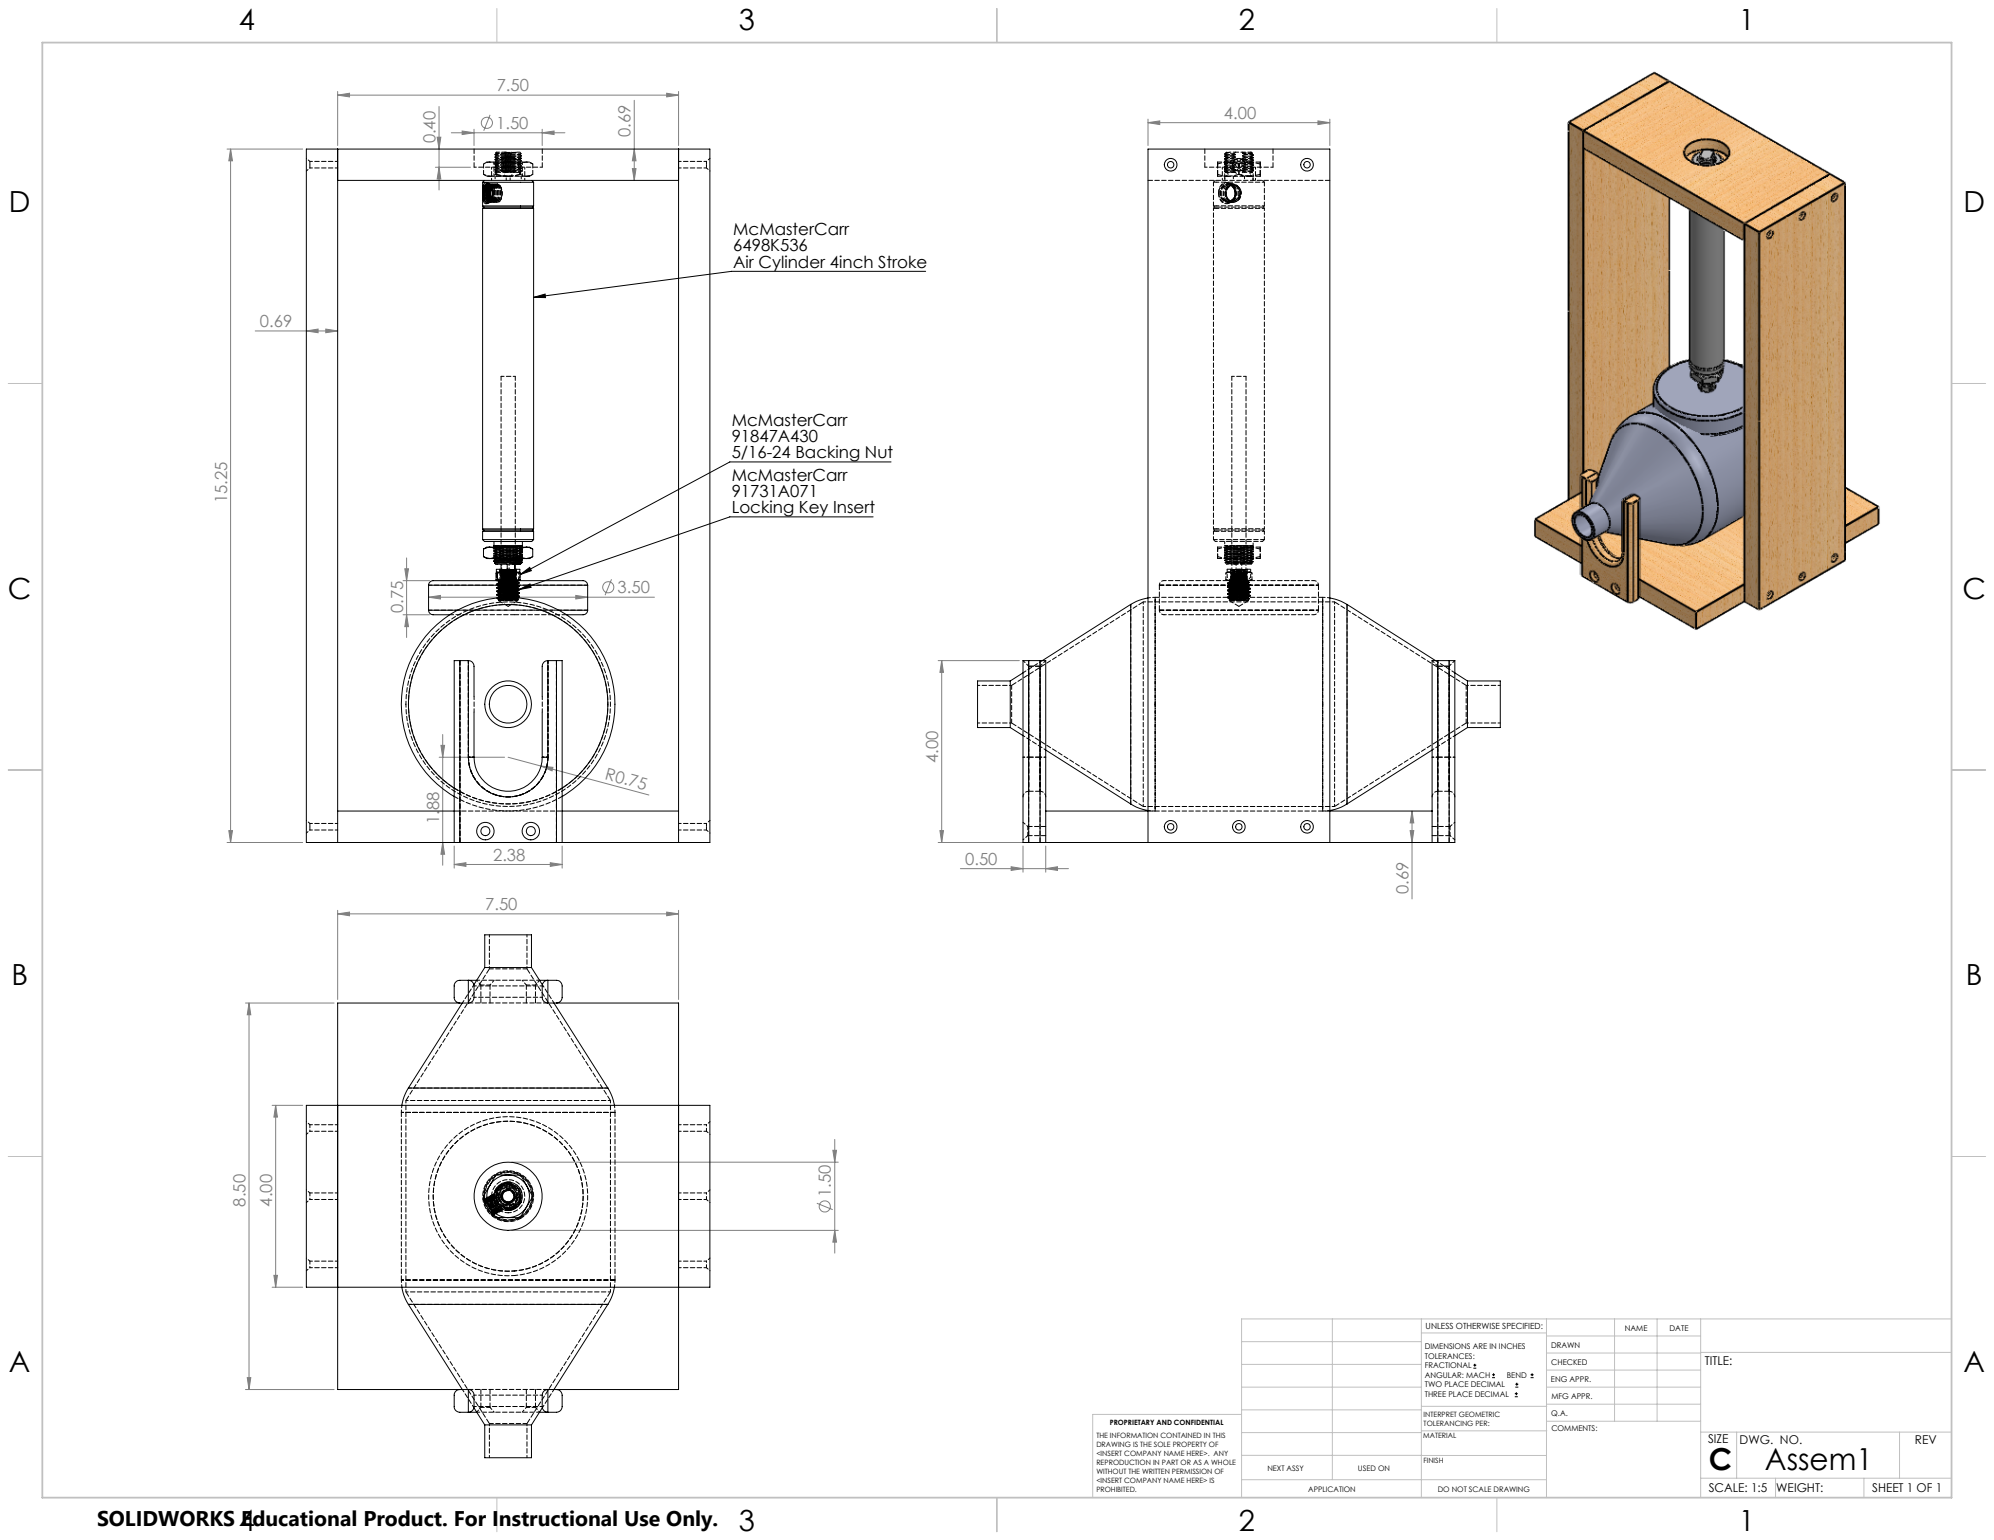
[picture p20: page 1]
Locking Key Insert; Air Cylinder 4inch Stroke; 5/16-24 Backing Nut

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

CHECKED | | | TITLE:

ENG APPR.
MFG APPR.

INTERPRET GEOMETRIC TOLERANCING PER: | Q.A.
MATERIAL | | SIZE C | DWG. NO. Assem1 | REV

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

NEXT ASSY | USED ON | FINISH

APPLICATION | DO NOT SCALE DRAWING | | SCALE: 1:5 | WEIGHT: | SHEET 1 OF 1

SOLIDWORKS Educational Product. For Instructional Use Only.

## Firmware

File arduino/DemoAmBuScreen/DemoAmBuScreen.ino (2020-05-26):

#include "SPI.h"
#include "Adafruit_GFX.h"
#include "Adafruit_ILI9341.h"

#define TFT_DC 9
#define TFT_CS -1
#define TFT_MOSI 12
#define TFT_MISO -1
#define TFT_RST 10
#define TFT_CLK 13
#define pin_relay 8
#define pin_switch 7
#define pin_encoderA 6 // D3
#define pin_encoderB 5 // D4

#define TFT_FONTH_1  8*1
#define TFT_FONTH_2  8*2
#define TFT_FONTH_3  8*3
#define TFT_FONTW    6


// Ventilator Parameters
// current, change_by, min, max
float pRR[]   = {20.0, 0.5, 10.0, 30.0};  // breaths/min
float pTH[]   = {-5.0, 0.1, -10.0, 0} ;   // cmH2O
float pIE[]   = {2.0, 0.05, 1.0, 2.5};    // in:out ratio
float pVol[]  = {500., 10., 200., 1000.}; // mL
float pVmax[] = {600., 10., 250., 1000};  // mL
float pPmax[] = {60., 2., 20., 100.};     // cmH2O
float pMin[]  = {0., 2., 0., 30.};        // cmH2O
float respPeriod = 0.;  // milliseconds
long rand_long = 0;
double randp_peep = 0.0;
double randp_pip = 0.0;
double randp_vol = 0.0;
long curTime = 0;
long measTime = 0;
long dispTime = 0;
long cycleTime = 0;
int cycleState = 0;  //0 closed,  1 open
int encoderVal = 0;
int encoderPushes = 0;
int current_p = 0;
const long encoderTDeadTime = 50; //millis
const long encoderPDeadTime = 500; //millis
long encoderPushTime = 0; //millis
long encoderTurnTime = 0; //millis
bool stateA, stateB;
const int TFT_w = 240;
const int TFT_h = 320;
char s[5];
long t0, tf, tm;

//Adafruit_ILI9341 tft = Adafruit_ILI9341(TFT_CS, TFT_DC, TFT_MOSI, TFT_CLK, TFT_RST, TFT_MISO);
Adafruit_ILI9341 tft = Adafruit_ILI9341(&SPI, TFT_DC, TFT_CS, TFT_RST);
void setup_display(){
  // Screen is 240x320
  // Clear screen
  tft.fillScreen(ILI9341_BLACK);
  tft.setTextSize(2);
  tft.setTextColor(ILI9341_BLUE);
  tft.setCursor(16, 1); // 40 - 12*2
  tft.print("PEEP");
  tft.setTextColor(ILI9341_GREEN);
  tft.setCursor(102, 1); // 120 - 12*1.5
  tft.print("PIP");
  tft.setTextColor(ILI9341_CYAN);
  tft.setCursor(182, 1);  // 200 - 12*1.5
  tft.print("Vol");
  // Values start at y=30
}

void update_display() {
  // Headers for display live parms starts on L1 and are font size 2
  // values that go below these labels:
  tft.setTextSize(3);
  tft.setTextColor(ILI9341_BLUE);
  tft.fillRect(0,30,80,TFT_FONTH_3,ILI9341_BLACK);
  tft.setCursor(1, 30);   // 40 - 18*2 - 3
  tft.print(randp_peep,1);
  //
  tft.setTextColor(ILI9341_GREEN);
  tft.fillRect(80,30,80,TFT_FONTH_3,ILI9341_BLACK);
  tft.setCursor(87, 30);   // 120 - 18*2 +3
  tft.print(randp_pip,1);
  tft.setTextColor(ILI9341_CYAN);
  tft.fillRect(160,30,80,TFT_FONTH_3,ILI9341_BLACK);
  tft.setCursor(173, 30);  // 200-18*1.5
  tft.print(randp_vol,0);
}


double get_rand(double rmin, double rmax){
  rand_long = random();
  return rmin + (rmax - rmin)* ((double)rand_long / 4.2949e9);
}


void setup() {
  Serial.begin(9600);
  //SPI.begin();

  Serial.println("Starting up");
  pinMode(pin_relay, OUTPUT);
  pinMode(pin_switch, INPUT_PULLUP);
  pinMode(pin_encoderA, INPUT_PULLUP);
  pinMode(pin_encoderB, INPUT_PULLUP);
  SPI.begin();
  tft.begin();
  tft.setRotation(0);
  respPeriod = 60. / pRR[0] * 1e3;  // millis
  Serial.println("Setup Done, running...");
  setup_display();
}

void loop() {
  curTime = millis();
  if ( (curTime - measTime) > 9 ){
    // Take a sudo measurments
    randp_peep = get_rand(11.0, 15.0);
    randp_pip  = get_rand(25.0, 31.0);
  }
  if ( cycleState == 0 ){
    // The valve is closed
    if ( (curTime - cycleTime) > ( (respPeriod / (1.0 + pIE[0])) * pIE[0] ) ){
      cycleState = 1;
      digitalWrite(pin_relay, HIGH);
      cycleTime = curTime;
      Serial.println("Breath in...");
      randp_vol  = get_rand(400.0, 455.0);
      t0 = millis();
      update_display();
      tf = millis();
      tm = millis();
      Serial.println(tf - t0 - (tm-tf));
    }
  }
  else if ( cycleState == 1 ) {
    if ( (curTime - cycleTime) > ( (respPeriod / (1.0 + pIE[0])) ) ){
      cycleState = 0;
      digitalWrite(pin_relay, LOW);
      cycleTime = curTime;
      Serial.println("Breath out...");
    }
  }
}

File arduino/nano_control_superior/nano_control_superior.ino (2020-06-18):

#include <Wire.h>
#include <AmbuConfig.h>
#include <CycleControl.h>
#include <SensorDlcL20D4.h>
#include <SensorSp110Sm02Flow.h>
#include <SensorVolume.h>
#include <stdint.h>
#include <HardwareSerial.h>
#include <Comm.h>
#include <Arduino.h>

#define RELAYA_PIN 8
#define RELAYB_PIN 7
#define REDLED_PIN 3
#define YELLED_PIN 4
#define PIEZO_PIN  2
#define PIN_12V A6
#define PIN_9V  A7
#define SENSOR_PERIOD_MILLIS 9
#define DISPLAY_PERIOD_MILLIS 999
//#define SerialPort Serial
#define SerialPort Serial1  // Interface to the MAX3232

// Uart on pin D9/10 for display communication
// https://stackoverflow.com/questions/57175348/softwareserial-for-arduino-nano-33-iot
#ifdef ARDUINO_ARCH_MBED
UART uart(digitalPinToPinName(5), digitalPinToPinName(6), NC,NC);
#elif  ARDUINO_ARCH_SAMD
#include "wiring_private.h"
Uart uart (&sercom1, 12, 11, SERCOM_RX_PAD_3, UART_TX_PAD_0);
// Attach the interrupt handler to the SERCOM
void SERCOM1_Handler()
{
    uart.IrqHandler();
}
#else
#error Unsupported Hardware
#endif

Comm displayComm(uart);    // To second NANO for local-display
Comm serComm(SerialPort);  // To MAX3232

AmbuConfig conf(serComm,displayComm);
SensorDlcL20D4 press;
SensorSp110Sm02Flow flow;
SensorVolume vol(flow);
CycleControl relay(conf,press,vol,RELAYA_PIN,RELAYB_PIN,REDLED_PIN,YELLED_PIN,PIEZO_PIN,PIN_12V,PIN_9V);


uint32_t sensorTime;
uint32_t displayTime;
void setup() {
#ifdef  ARDUINO_ARCH_SAMD
     pinPeripheral(11, PIO_SERCOM);
     pinPeripheral(12, PIO_SERCOM);
#endif
   SerialPort.begin(57600);
   uart.begin(9600);
   Serial.begin(57600);
   Message m;
   m.writeString(Message::DEBUG,millis(),"Booted");
   serComm.send(m);

   Wire.begin();

   relay.setup();

   // Wait 5 seconds for pressure to settle
   m.writeString(Message::DEBUG,millis(),"Wait 5 seconds");
   serComm.send(m);
   delay(5000);

   conf.setup();
   press.setup();
   flow.setup();
   vol.setup();

   sensorTime = millis();
   m.writeString(Message::DEBUG,millis(),"Setup Done");
   serComm.send(m);
}

void loop() {
   uint32_t currTime=millis();

   if ((currTime - sensorTime) > SENSOR_PERIOD_MILLIS ) {

      press.update(currTime);
      flow.update(currTime);
      vol.update(currTime);
      float sendFloat[5];
      uint32_t sendInt[2];
      sendFloat[0]=relay.prevVmax();
      sendFloat[1]=relay.prevPmax();
      sendFloat[2]=press.scaledValue();
      sendFloat[3]=flow.scaledValue();
      sendFloat[4]=vol.scaledValue();
      sendInt[0]=relay.cycleCount();
      sendInt[1]=relay.status();
      // Update display every second
      Message m;
      m.writeData(Message::DATA,currTime,5,sendFloat,2,sendInt);
      serComm.send(m);
      sensorTime = currTime;
   }
   // Update display every second
   if ((currTime - displayTime) > DISPLAY_PERIOD_MILLIS )  {
     Message m;
      float sendFloat[9];
      float parms[6];
      sendFloat[0]=relay.prevPmin();
      sendFloat[1]=relay.prevPmax();
      sendFloat[2]=relay.prevVmax();
      sendFloat[3]=conf.getRespRate();
      sendFloat[4]=conf.getInhTime();
      sendFloat[5]=conf.getVolInThold();
      sendFloat[6]=conf.getVolMax();
      sendFloat[7]=conf.getPeepMin();
      sendFloat[8]=conf.getPipMax();
     m.writeData(Message::DATA,currTime,9,sendFloat,0,0);
     displayComm.send(m);
     displayTime=currTime;
   }



   relay.update(currTime);
   conf.update(currTime,relay);

}

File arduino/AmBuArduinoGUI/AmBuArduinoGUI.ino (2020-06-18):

#include "Arduino.h"
#include "SPI.h"
#include "Adafruit_GFX.h"
#include "Adafruit_ILI9341.h"
#include "GUI.h"
#include "Comm.h"
#include "AmbuConfig.h"

#define SerialPort Serial1 //RX-TX pins on board
Comm masterComm(SerialPort);

#define SPI_DEFAULT_FREQ 20000000

//encoder
#define pin_switch 7
#define pin_encoderA 6
#define pin_encoderB 5

float update_parms[nParam] = {0.f};

//gets data from master
float parms[nParam]={0.f};

GUI_value gui_value[nParam]={
  {name:"PEEP",  //Last cycle min pressure
   id:pPEEP,
   ambucfg:0,
   val:&parms[pPEEP],
   dval:10.0f, 
   dx:2.0f, 
   min:0.0f, 
   max:90.0f,
   fmt:"%02.1f"
  },
  {name:"PIP",  //last cycle max pressure
   id:pPIP,
   ambucfg:0,
   val:&parms[pPIP],
   dval:30.0f, 
   dx:2.0f, 
   min:00.0f, 
   max:50.0f,
   fmt:"%02.1f"
  },
  {name:"Vol",  // last cycle volume mL
   id:pVol,
   ambucfg:0,
   val:&parms[pVol],
   dval:500.0f, 
   dx:10.0f, 
   min:000.0f, 
   max:1000.0f,
   fmt:"%3.0f"
  },
  {name:"RR",    // resp rate in Hz
   id:pRR,
   ambucfg:AmbuConfig::SetRespRate,
   val:&parms[pRR],
   dval:20.0f, 
   dx:0.5f, 
   min:10.0f,
   max: 30.0f,
   fmt:"%02.1f"
  },
  {name:"IH",    //Inhale time in seconds
   id:pIH,
   ambucfg:AmbuConfig::SetInhTime,
   val:&parms[pIH],
   dval:1.0f,
   dx: 0.1f, 
   min:  0.5f, 
   max : 2.5f,
   fmt:"%02.1f"
  },
  {name:"TH",    //threhsold cmH2O
   id:pTH,
   ambucfg:AmbuConfig::SetVolInThold,
   val:&parms[pTH],
   dval:0.0f,       
   dx:0.1f, 
   min:-10.0f, 
   max:30.0f,
   fmt:"% 2.1f"
  },
  {name:"Vmax",  //Threshold where volume will stop IH short
   id:pVmax,
   ambucfg:AmbuConfig::SetVolMax,
   val:&parms[pVmax],
   dval:800.0f, 
   dx:10.0f, 
   min:250.0f, 
   max:990.0f,
   fmt:"%3.0f"
  },
  {name:"Pmin",  //Threshold where pressure will alarm
   id:pPmin,
   ambucfg:AmbuConfig::SetPeepMin,
   val:&parms[pPmin],
   dval:-10.0f, 
   dx:2.0f, 
   min:-10.0f, 
   max:30.0f,
   fmt:"% 2.1f"
  },
  {name:"Pmax",  //Threshold where pressure will alarm
   id:pPmax,
   ambucfg:AmbuConfig::SetPipMax,
   val:&parms[pPmax],
   dval:10.0f, 
   dx:2.0f, 
   min:10.0f, 
   max:60.0f,
   fmt:"%02.1f"
  }
};

GUI gui;

void setup_display(){
  //uint8_t fs = 2;
  uint16_t  y = 10; 
  uint16_t x;
  uint16_t vspace = 25;
  uint16_t hspace = 5;
  x =  hspace;
  gui.addItem( gui_value[pPEEP], {x,y,ILI9341_PINK,3,ILI9341_PINK,3,false,false});   
  x =  GUI::TFT_THIRD + hspace;
  gui.addItem(gui_value[pPIP],  {x,y,ILI9341_GREENYELLOW,3,ILI9341_GREENYELLOW,3,false,false});   
  x =  2*GUI::TFT_THIRD + hspace;
  gui.addItem( gui_value[pVol], {x,y,ILI9341_CYAN,3,ILI9341_CYAN,3,false,false});   
  y =  1 + 8*3 + 8*3 + 7 + vspace;
  x = 3*hspace;
  gui.addItem( gui_value[pRR], {x,y,ILI9341_WHITE,2,ILI9341_WHITE,2,false,false});
  x =  GUI::TFT_THIRD + hspace;
  gui.addItem( gui_value[pIH], {x,y,ILI9341_WHITE,2,ILI9341_WHITE,2,false,false});
  x =  2*GUI::TFT_THIRD + hspace;
  gui.addItem( gui_value[pTH], {x,y,ILI9341_WHITE,2,ILI9341_WHITE,2,false,false});
  y =  1 + 8*3 + 8*3 + 7 + 14 + 8*2 + 7 + 8*2 + vspace;
  x = 3*hspace;
  gui.addItem( gui_value[pVmax], {x,y,ILI9341_WHITE,2,ILI9341_WHITE,2,false,false});
  x =  GUI::TFT_THIRD + hspace;
  gui.addItem( gui_value[pPmin], {x,y,ILI9341_WHITE,2,ILI9341_WHITE,2,false,false});
  x =  2*GUI::TFT_THIRD + hspace;
  gui.addItem( gui_value[pPmax], {x,y,ILI9341_WHITE,2,ILI9341_WHITE,2,false,false});
  gui.setup();
} 

void update_display() {
  gui.update();
}


void setup() {
  asm(".global _printf_float");
  asm(".global _scanf_float");
  SerialPort.begin(9600);
  Serial.begin(9600);
  Serial.print("startup\n");
  // Encoder Pins
  pinMode (pin_encoderA, INPUT_PULLUP);
  pinMode (pin_encoderB, INPUT_PULLUP);
  pinMode (pin_switch, INPUT_PULLUP);

  setup_display();
  delay(2000);
}


uint32_t measTime = 0;
unsigned counter=0;
char s[64];
uint32_t curTime;
int8_t encDT;   // -1 for CCW, +1 for CW turn
bool encPushed;
int8_t guiParamSelected = -1;  //-1 for non and 0... for n
const uint32_t guiTimeout = 10000; //millis till gui times out
uint32_t guiPrevActionTime;
const uint32_t encTDeadTime = 100; //millis
const uint32_t encPDeadTime = 500; //millis
long encLastPTime = 0; //millis
long encLastTTime = 0; //millis
bool stateA, stateB;


void loop() {
  curTime = millis();
  //
  // Check encoder for update
  //
  encDT = 0;
  encPushed = false;
  if ( digitalRead(pin_switch) == false ) {
    if (curTime - encLastPTime > encPDeadTime) {
      encLastPTime = curTime;
      //Serial.println("Switched");
      encPushed = true;
    }
  }
  stateA = digitalRead(pin_encoderA);
  stateB = digitalRead(pin_encoderB);
  if (stateA == false  &&  encPushed == false) {
    // Here deal with turned encoder input.
    // I dont want to process pushes and turns at the same
    // time since they shouldn't happen in the same cycle. 
    if (curTime - encLastTTime > encTDeadTime) {
      encLastTTime = curTime;
      if (stateB != stateA) encDT = -1;
      else encDT = 1;
    //Serial.println(encDT);
    }
  }
  if (encDT!=0 || encPushed) {
    // update the timeout timer since some input was recieved
    guiPrevActionTime = curTime;
  }
  //
  // Take actions based on encoder input
  //
  if ( encDT != 0 ) { 
    // The encoder was turned in either direction
    if (guiParamSelected == -1) {
      // if no parameter is selected, select the first
      guiParamSelected = 3;
      gui.items[guiParamSelected].elem.highlight = true;
    }
    else {
      // A parameter is activly selected or highlighted
      if (gui.items[guiParamSelected].elem.highlight == true) {
        // the parameter is only highlighted
        // turning encoder should move to the next parameter
        // change the previous selected one to unhighlighted:
        gui.items[guiParamSelected].elem.highlight = false;
        guiParamSelected = guiParamSelected + encDT;
        // guiParamSelected should always be in the range 3-8
        if (guiParamSelected < 3)       guiParamSelected = 8;
        else if (guiParamSelected > 8)  guiParamSelected = 3; 
        // hightlight the new parameter 
        gui.items[guiParamSelected].elem.highlight = true; 
      }
      else if (gui.items[guiParamSelected].elem.selected) {
        // the parmater is selected and the value should be changed
        gui.change_value(guiParamSelected, encDT);
        // Send the changed value to AmBuConfig
        uint32_t intData[2];
        intData[0]=gui_value[guiParamSelected].ambucfg;
        float floatData=parms[guiParamSelected];
	      Message msg;
        Serial.print("Sending MSG: ");
        Serial.print(intData[0]);
        Serial.println(floatData);
        msg.writeData(Message::PARAM_FLOAT,0,1,&floatData,1,intData);
        masterComm.send(msg);
      }
    }
    update_display();    
  }

  else if (encPushed) {
    if (gui.items[guiParamSelected].elem.highlight) {
      gui.items[guiParamSelected].elem.highlight = false;
      gui.items[guiParamSelected].elem.selected = true;
    }
    else if (gui.items[guiParamSelected].elem.selected) 
    {
      gui.items[guiParamSelected].elem.highlight = true;
      gui.items[guiParamSelected].elem.selected = false;
    }
    update_display();
  }
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

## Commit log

2020-04-07 Update new pressure sensor
2020-04-14 Update arduino
2020-04-23 Flow cal fix
2020-04-29 Quick hack to try SP110 dP sensor
2020-05-10 hard-wire paths
2020-05-11 Fix flow vs press
2020-05-15 take timestamp from arduino
2020-05-19 added arduino uptime to gui
2020-05-20 includes draft of calibrations page. Parts are commmented to avoid duplicates of widgets, which are causing problems on other pages.
2020-05-22 added text and some calibration steps functionality to calibrations page
2020-05-22 update to calibrations page, including first set of instructions with functionality. Parts are again commmented to avoid duplicates of widgets, which are causing problems on other pages.
2020-05-24 Making progress, this worked on IOT but sprintf bug prevents values from being print.
2020-05-24 serial prints what I think it should, but not working. The display only shows the first 3 labels for me after the loop runs update.
2020-05-29 Support board serial
2020-05-29 remove json files - add board name to compile scripts - fix mbed compilation
2020-05-29 fix board upload script
2020-05-30 Add support for second valve
2020-06-01 rebase, include 2nd valve
2020-06-05 Propoer shutdown of the queue manager thread
2020-06-11 put queue between QT and serial handling thread
2020-06-14 added arduino vmax function from issue83
2020-06-14 better, update all parameters except the currently adjusted one
2020-06-27 fix corner case when cycling through alarms displayed in banner
2020-06-27 clean up GUI add device serial, SW version and com port
2020-06-27 move sample rate to About tab
2020-07-07 Add pressure run mode
2021-03-29 Add main directory
    [List of IP for ASV.xlsx]
2021-03-29 Upload 3-D printed parts
    [PEEP to PIP converter 26mm.STEP, PEEP to PIP converter 26mm.STL, SensorBoard2_Lid.STL, SensorBoard2_LowerBox.STL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]
2021-03-29 Upload electronics
    [NanoShield_V03.sch, PCB NanoV03 BOM.xlsx]
2021-03-29 Upload frame and pneumatics
    [Mechanical parts BOM.xlsx]
2021-03-29 Upload media materials
2021-03-29 Upload patient circuit and photos of parts
    [Patient circuit BOM.xlsx]
